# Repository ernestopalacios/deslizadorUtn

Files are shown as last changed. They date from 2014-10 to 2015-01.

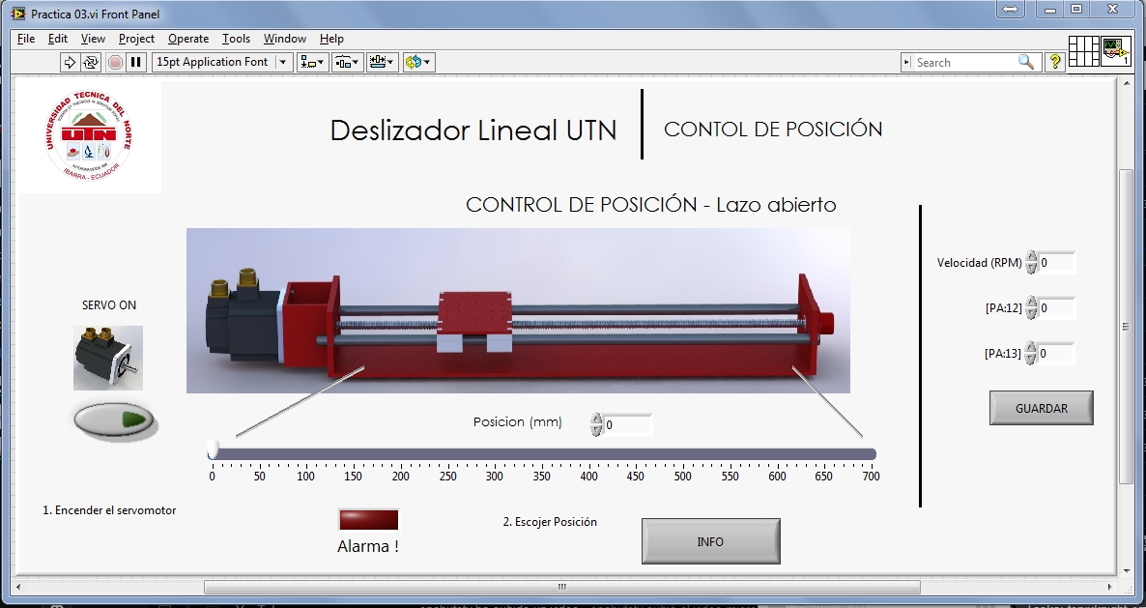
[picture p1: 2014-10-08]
deslizador/SolidW_Final/Renders/Programa/Practica 03.png

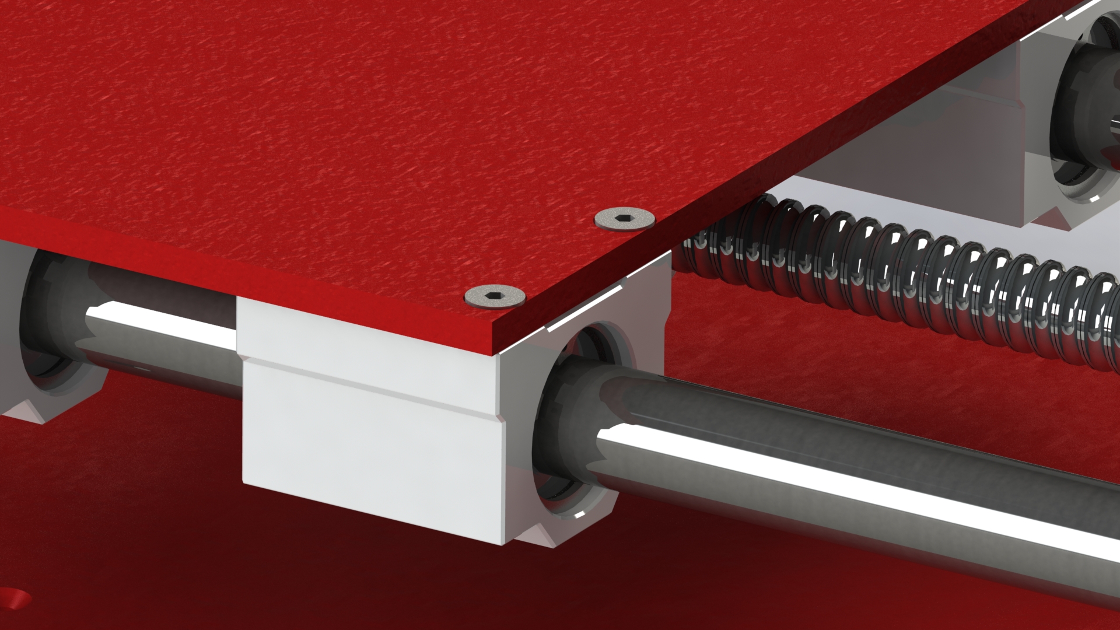
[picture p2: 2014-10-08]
deslizador/SolidW_Final/Renders/detalle_02.JPG

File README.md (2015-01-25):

DeslizadorUtn
=============

Repositorio para el deslizador lineal desarrollado para la Universidad Técnica del Norte.

Manual de ayuda: https://github.com/ernestopalacios/deslizadorUtn/wiki

El reposito esta dividido en las siguientes carpetas:

---> deslizador :  Archivos del deslizador en SolidWorks 2013

---> deslizadorlineal : Documentación del trabajo de grado.

---> labview : Libreria para el control del servomotor en LABVIEW.

---> mbed : Documentacion microcontrolador.

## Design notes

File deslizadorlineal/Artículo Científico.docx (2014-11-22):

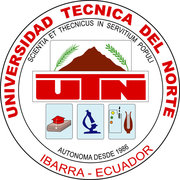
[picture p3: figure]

UNIVERSIDAD TÉCNICA DEL NORTE

FACULTAD DE INGENIERÍA EN CIENCIAS APLICADAS

CARRERA DE INGENIERÍA EN MECATRÓNICA

ARTÍCULO CIENTÍFICO

TEMA:

SISTEMA MODULAR PARA REALIZAR PRÁCTICAS DE SERVOMECANISMOS Y CONTROL MEDIANTE DESLIZADOR LINEAL E INTERFAZ CON LABVIEW

AUTOR: Ernesto Vladimir Palacios Merino

DIRECTOR: Ing. Diego Terán

Ibarra - Ecuador

2014

[^1]

SISTEMA MODULAR PARA REALIZAR PRÁCTICAS DE SERVOMECANISMOS Y CONTROL MEDIANTE DESLIZADOR LINEAL E INTERFAZ CON LABVIEW

Palacios Merino, Ernesto Vladimir

mecatronica.mid@gmai.com

Universidad Técnica del Norte

Resumen—El presente trabajo describe el diseño e implementación de un deslizador lineal, el mismo que ha sido acoplado para su uso con el servomotor GSK 110SJT. Para llevar a cabo el control de este mecanismo se han creado librerías e interfaces en el lenguaje de programación gráfico de LabVIEW, dichas librerías han sido elaboradas con el ánimo de que brinden a los estudiantes de mecatrónica de la Universidad Técnica del Norte, facilidad de uso y escalabilidad en sus proyectos, animando a la creación de programas y mecanismos más elaborados. Una vez que se ha completado la parte mecánica, eléctrica y electrónica se cuenta con un sistema, en el cual se interrelacionan todos sus módulos y subsistemas, a través de una librería y protocolos de comunicación definidos, pudiendo de esta manera llevar a cabo prácticas de servomecanismos y control.

Índice de Términos—LabVIEW (Plataforma de desarrollo virtual gráfico). API (Application Programming Interface)

E

# I. INTRODUCCIÓN

l presente trabajo de grado describe el diseño e implementación de un sistema modular para realizar prácticas de servomecanismos y control. El objetivo del mismo es que tener mayor facilidad de uso de los para los servomotores GSK 110SJT, se han desarrollado cuatro prácticas en las cuales los estudiantes podrán familiarizarse con el sistema y con el control que se puede ejercer sobre la misma.

El recorrido del deslizador es de 80 centímetros dentro de los cuales se ha destinado dos sensores ópticos a cada extremo del deslizador los cuales sirven de advertencia y protección ante eventuales colisiones que puedan sucederse por una mala operación del equipo.

El sistema electrónico permite el control del servodrive a través de una comunicación serial RS-232, o mediante una red de datos TCP/IP. Estas dos formas de comunicación brindan gran flexibilidad en el manejo del dispositivo.

El sistema se subdivide en tres partes claramente diferenciadas, el subsistema mecánico, el subsistema electrónico y el subsistema informático. En la base del subsistema mecánico se encuentra el tornillo de bolas re-circulantes, el cual junto a las guías y rodamientos permiten el movimiento lineal del deslizador. El tornillo utilizado permite tener una precisión de 52um, el servomotor utilizado cuenta con 10 000 pasos por revolución, lo que se traduce a una precisión de 0.5um, la cual se ve limitada por la precisión del tornillo.

El segundo subsistema, el electrónico, cuenta como elemento principal el microcontrolador ARM mbed® el cual actúa como puente entre el subsistema informático y el subsistema mecánico, este elemento permite la ejecución de comandos enviados a través de sus interfaces seriales, o de su interfaz ethernet, permitiendo el control del deslizador de una manera sencilla.

El subsistema informático es aquel que se encuentra expuesto directamente al usuario, se ha creado para ello una interfaz para su programación (API), mediante la cual se puede interactuar con el servomotor y consecuentemente con el deslizador, esta API se ha desarrollado sobre el lenguaje de programación de LabVIEW, sin embargo debido a la característica de comunicación serial del dispositivo estas librerías pueden ser exportadas a otros lenguajes de programación.

# II. Desarrollo de Contenidos

## A. Diseño del sistema

La transmisión de potencia desde el servomotor hacia el carro deslizador se lo realiza a través del tornillo central, el cual se ha determinado como un tornillo de bolas re-circulantes el cual permitirá contar con la precisión necesaria para la implementación de este trabajo, además de minimizar el juego existente entre la tuerca y el tornillo.

Para facilitar el movimiento del carro deslizador se ha escogido rodamientos lineales, los cuales proveen de un bajo coeficiente de fricción además de soportar la fuerza ejercida por la carga. Estos rodamientos requieren de guías de acero rectificado las cuales brindarán una larga vida útil a los rodamientos.

La estructura para soportar el mecanismo se ha elaborado en acero ASTM A-500, permitiendo soportar todas las fuerzas generadas y brindando la rigidez necesaria para el buen desempeño del deslizador para la carga propuesta la cual es de 30 Kg.

## B. Características mecánicas.

El rodamiento lineal escogido es el SKF LBBR 20, el cual soporta una carga estática de 800 Newtons. El tiempo de vida útil calculado para una carga de 588 Newtons es de 176 Km de recorrido de acuerdo a la siguiente ecuación:

L_10 =(l_s)/(l_t)(C/P)^p L_10 =0.7/1(800/588)^3

L_10 =1.76 ∙10^5 (m)

Se ha utilizado dos rodamientos por guía, con un total de cuatro rodamientos. El tornillo tiene una longitud total de 1000 mm, un diámetro externo de 16 mm y una longitud de paso de 5mm, se cuenta con una eficiencia del 90% y un coeficiente de fricción de 0.05% con lo cual cumple con los requisitos necesarios para esta aplicación.

Para calcular la inercia del eje contamos con la siguiente fórmula:

J_(eje) =(7.57x10^(-13) )D^4 L kg-m^2

Dónde.

J = Inercia en el eje

D = Diámetro del eje

L = Longitud del eje

Utilizando los valores de la hoja de datos del tornillo obtenemos:

J_(eje) =(7.57x10^(-13) )(16)^4 (1000) (kg.m^2 ) J_(eje) =4.96x10^(-5) (kg.m^2 )

La inercia de la carga es la siguiente:

J_(eje) =(2.25x10^(-8) )(m_(carga))/(P^2) kg-m^2

Dónde.

J_(carga) = Inercia de la carga reflejada en kg.m2

m_(carga) = Carga útil en kg a:

P = paso del eje expresado en rev/mm

Utilizando los valores de este proyecto tenemos:

J_(eje) =(2.25x10^(-8) )30/(0.2^2) ( kg.m^2 ) J_(eje) =1.6875 x 10^(-5) (kg.m^2 )

J_(eje) =(7.57x10^(-13) )(16)^4 (1000) (kg.m^2 ) J_(eje) =4.96x10^(-5) (kg.m^2 )

J_(TOTAL) =(1.6875+4.96)x10^(-5) (kg.m^2 ) J_(TOTAL) = 6,6475 ( kg.m^2 )

El torque para la aceleración, tomando en cuenta la carga utilizada, la inercia en el motor y la eficiencia obtenemos el siguiente resultado.

T_α =(J_(motor) +(J_(eje))/e+(J_(carga))/e)α N.m

Dónde:

e = Eficiencia

J_(motor) = Inercia del motor (típico 0.5)

T_α =(0.5+6.6475/0.9)x10^(-5) (11310) (N.m) T_α =0,89 (N.m)

El torque generado por el servomotor es de dos Newton por metro, con lo cual podrá funcionar sin ningún inconveniente.

## C. Características electrónicas.

El subsistema electrónico tiene como base al microcontrolador LPC1768 el cual implementa la plataforma de desarrollo ARM mbed. Este microcontrolador interactúa con el servodrive mediante señales eléctricas, el servodrive es el elemento que controla al servomotor. El microcontrolador está conectado al encoder y a los sensores de proximidad del deslizador.

Los sensores de proximidad están colocados de tal manera que el carro deslizador no golpee los extremos del deslizador y evite que sea dañado por una mala manipulación. Se ha implementado un sensor de advertencia y uno de error para cada extremo del deslizador, esto permite al programador tomar acciones correctivas y de no hacerlo el sensor de error actúa y detiene al servomotor.

El encoder implementado es un encoder absoluto de cuadratura HOHNER, el cual cuenta con una resolución de 360 pulsos por revolución, al ser conectado al microcontrolador puede multiplicar la resolución por cuatro, esto se puede lograr debido a los dos canales, A y B del encoder dando una resolución de 1440 pulsos por resolución, lo cual se traduce a una precisión de 3.472 micrones.

El subsistema electrónico tiene dos fuentes de energía una de 24 VDC y otra de 5 VDC, la fuente de 24 VDC se utiliza para la alimentación del encoder y la generación de una señal analógica de voltaje para el control de velocidad del servomotor, la fuente de 5 VDC es utilizada para la alimentar el microcontrolador.

El microcontrolador implementa para la comunicación dos puertos seriales, uno a través de USB y otro a través de un conector DB-9, también se implementa un puerto de comunicaciones ethernet, con el cual se puede conectar el microcontrolador a una red de datos cableada.

## D. Características de software

Las opciones de comunicación implementadas por el microcontrolador simplifican en gran medida el control del servomotor, tomando ventaja de este hecho se ha diseñado un listado de comandos que el microcontrolador puede ejecutar para el control del servomotor.

TABLA I

Listado de comandos para la comunicación con el microcontrolador ARM MBED
Comando | Valores aceptables | Detalle
S | 0 a 1 | Apagar / Encender el servomotor
H | 0 a 500000 | Frecuencia de salida del tren de pulsos, en hertzios.
K | 0 a 500 | Frecuencia de salida del tren de pulsos, en kilohertzios.
D | 0 a 1 | Sentido de giro: (CW = 1 – Hacia el motor). (CCW = 0 – Hacia el encoder).
A | -10000 a +10000 | Voltaje de salida de +-10V con una resolución de ~4.8mV.
P | 0 a 2 147 483 647 | Número predefinido de pulsos
M | 0 a 2 147 483 647 | Generar un número predefinido de pulsos, multiplica el valor del comando por mil
N | 0 a 2 147 483 647 | Generar un número predefinido de pulsos, multiplica el valor del comando por un millón
V | 10 - 500000 | La velocidad en tren de pulsos a la cual se va a llegar al ángulo deseado para el eje del motor.
I | 0 a 2 147 483 647 | Lleva el carro al inicio del recorrido. El valor numérico determina la frecuencia del tren de pulsos
E | 0 a 1 | 0 Leer posición actual. 1 Leer velocidad actual.
Z | 0 | Limpia el contador del encoder

El microcontrolador ejecutará estos comandos siempre y cuando lleguen en el formato correcto.

[int32]-[Comando][Enter]

[int32] = Cualquier número entero de 32bits.

[Comando] = Letra mayúscula que designa una acción a realizar.

[Enter] = Carácter Retorno de carro para enviar el comando.

Ejemplo de comandos aceptables:

1500-H

-125000000-P

0-E

-1-R

Se ha implementado una librería en el lenguaje de programación LabVIEW que permite a los estudiantes la interacción con el servomotor, esta librería actúa como una Interfaz de programación sobre la cual los estudiantes pueden desarrollar sus proyectos.

Esta librería se ha desarrollado en dos versiones, una para la comunicación serial y una para la comunicación ethernet, lo que permite esta librería es tener bloques de programación sencillos con los cuales se puede elaborar programas más complejos.

# III. Resultados Obtenidos

Mediante la aplicación de todo lo hasta aquí expuesto se tiene el resultado final el cual se muestra a continuación.

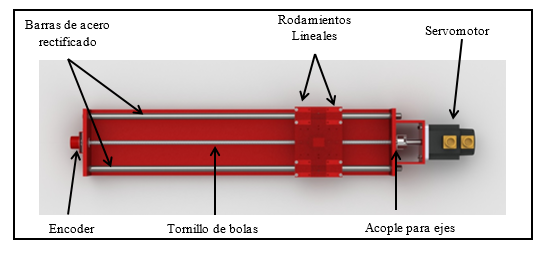
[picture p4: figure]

Fig. 1. Subsistema Mecánico.

El subsistema mecánico ensamblado, el servomotor es sujetado a la estructura del deslizador y unido al tornillo central mediante el uso de un matrimonio mecánico, de esta manera el tornillo central girará conjuntamente con el eje del servomotor. El carro deslizador se encuentra sujeto a la nuez del tornillo transmitiendo el torque rotacional del servomotor en movimiento, el peso que se aplica sobre el carro deslizador mismo es soportado por las guías laterales sobre las cuales se montan los rodamientos lineales facilitando su movimiento. Al final del tornillo de bolas se ubica el encoder, el cual gira junto con el eje del tornillo y del servomotor sirviendo de esta manera como sensor de retroalimentación al sistema.

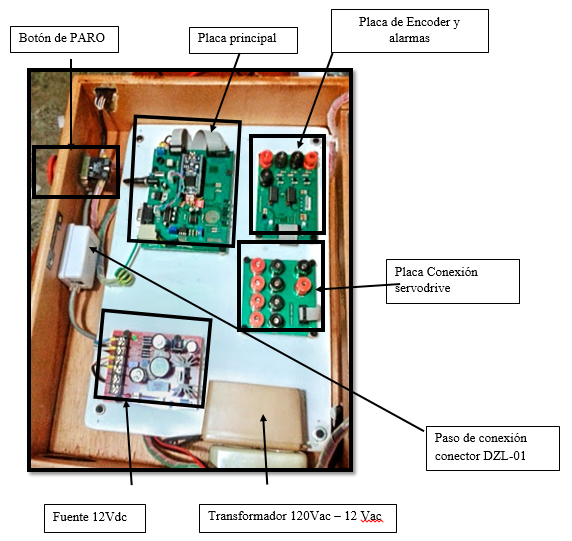
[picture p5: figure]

Fig. 2. Subsistema Electrónico

La implementación del subsistema electrónico cuenta con tres placas electrónicas, cada una desempeñando una función específica. La primera es la placa de conexión con el servodrive, la cual sirve para realizar las conexiones eléctricas con el servodrive. La segunda es la placa de encoder y alarmas, esta tiene la función de conectar el encoder y los sensores de proximidad ópticos, adapta su voltaje e implementa un circuito de protección independiente al microcontrolador principal para los casos en los que el carro del deslizador se acerque demasiado a los extremos del servomotor. Finalmente tenemos nuestra placa principal que es aquella en la que está montado el microcontrolador, en esta se tiene los puertos de comunicación con los dispositivos exteriores y en la cual se configura el modo de operación del subsistema.

El subsistema cuenta con dos modos de comunicación, serial y ethernet, sin embargo el microcontrolador solo puede trabajar con uno de ellos a la vez, por tal motivo es necesario configurar el puerto con el cual se va a trabajar. Para el modo de comunicación serial tenemos dos puertos, USB y conector DB-9, el puerto USB puede ser conectado directamente a un computador, sin embargo la longitud del cable queda restringida al estándar USB, para superar este problema se encuentra implementado el puerto DB-9, el cual cumple con los estándares RS-232 y puede ser extendido hasta una longitud de varios metros, dependiendo de la protección del cable utilizado. En el modo de comunicación ethernet se tiene un conector RJ-45 el cual permite al dispositivo ser conectado a un ruteador con el protocolo DHCP habilitado para que de esta manera el dispositivo pueda obtener una dirección IP válida y se pueda realizar la comunicación con el microcontrolador.

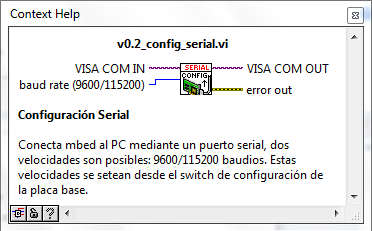
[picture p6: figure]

Fig. 3. Subsistema de Control

Finalmente tenemos el subsistema de control, implementado a través de la API creada para este efecto, la misma que ha sido desarrollada para el lenguaje LabVIEW. Esta librería permite controlar todos los aspectos fundamentales del dispositivo y ha sido escrita en dos versiones, una para cada modo de comunicación, tenemos la librería de comunicación serial y la librería de comunicación ethernet. Ambas librerías son simétricas, es decir que por cada función implementada en la librería serial se tiene su contraparte en la librería ethernet.

Además del control básico de los comandos enviados al servomotor estas librerías poseen funciones de reconocimiento de errores y generación de alarmas, lo cual facilita al estudiante el tomar acciones correctivas de acuerdo a los eventos generados.

Una vez que sistema modular se encuentra operativo se realizó algunas pruebas para comprobar el correcto funcionamiento de todos los subsistemas, encontrándose los siguientes resultados.

Tabla II

Pruebas de posición
N° Prueba | Carga (Kg) | Error medido (mm)
1 | 0 | > 0.01
2 | 5 | > 0.01
3 | 10 | > 0.01
4 | 15 | > 0.01
5 | 20 | > 0.01
6 | 25 | > 0.01
7 | 30 | > 0.01

El servomotor cuenta con dos modos de funcionamiento, uno de control de posición el cual es muy preciso y un modo de control de velocidad, para aplicaciones en las que se requiere de un torque constante.

En la Tabla 1 se analiza el error medido cuando el deslizador es sometido a diferentes cargas, obteniendo un resultado mejor al requerido por el alcance de nuestra aplicación. Esto es completamente esperado debido a la precisión tanto del servomotor como al juego casi inexistente en el tornillo.

Tabla III

Pruebas de velocidad
Voltaje aplicado (Vdc) | Velocidad esperada | Velocidad Medida (RPM)
10.00 | 2000 | 2000
5.00 | 1000 | 1150
2.00 | 400 | 452
1.00 | 200 | 218
0.00 | 0.00 | 0
-1.00 | -200 | -217
-2.00 | -400 | -450
-5.00 | -1000 | -1150
-10.00 | -2000 | -2000

En el modo de control de velocidad el servomotor se controla por medio de una salida de voltaje, para las mediciones se ocupó un multímetro FLUKE 83V calibrado con una precisión de cuatro cifras significativas, la medición de la velocidad fue tomada mediante el sensor del servodrive y se desconectó el carro deslizador del tornillo para tomar varias mediciones sin que el carro golpeé el final del deslizador. En este caso se puede apreciar que la velocidad medida no corresponde exactamente con el valor esperado, esto puede deberse a que el sensor de voltaje en el servodrive se encuentra descalibrado. Este error inherente en el servomotor abre la posibilidad de implementar métodos de control que permitan estudiar, minimizar y eliminar el error con el control de velocidad del sevomotor.

# IV. Practicas

El objetivo de este proyecto es la utilización del sistema modular por parte de los estudiantes, por tal motivo se ha desarrollado cuatro prácticas con las cuales se espera que el estudiante se familiarice con el manejo y programación del módulo. Estas prácticas exponen al estudiante con todas las posibilidades brindadas por el sistema y alientan a su modificación y observación de resultados. Todas las prácticas se ofrecen a través del modo de comunicación serial.

## A. Práctica 01. Generación de frecuencia

En la primera práctica se presenta al estudiante con el control del servomotor en su modo de posición. En este modo de control el subsistema electrónico genera un tren de pulsos, la frecuencia de este tren de pulsos determina la velocidad del servomotor, la dirección del giro es controlada por una salida digital.

El estudiante es presentado con una interfaz de fácil manejo en la cual controlan el encendido y apagado del servomotor, la frecuencia del tren de pulsos generados, y la dirección de giro del servomotor.

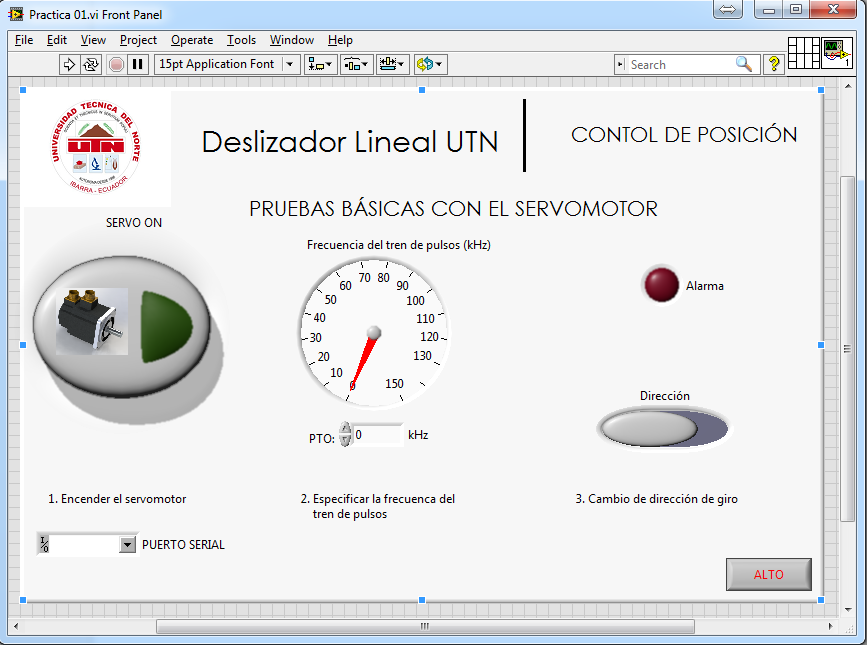
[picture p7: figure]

Fig. 4. Panel Frontal – Control de Posición.

Para el correcto funcionamiento de la práctica se requiere que el estudiante configure de manera adecuada los parámetros del servomotor, la comunicación serial y las conexiones eléctricas del servodrive, para completar estos pasos es necesario que el estudiante conozca estos aspectos básicos del sistema con lo cual se tiene una introducción a los conceptos básicos del manejo del servomotor y del sistema que se ha diseñado para su control.

## B. Práctica 02. Generación de voltaje

Esta práctica es similar a la primera práctica, sin embargo el modo de funcionamiento del servomotor es control de velocidad, en esta práctica el subsistema electrónico genera una señal de voltaje variable que controla la velocidad rotacional del servomotor.

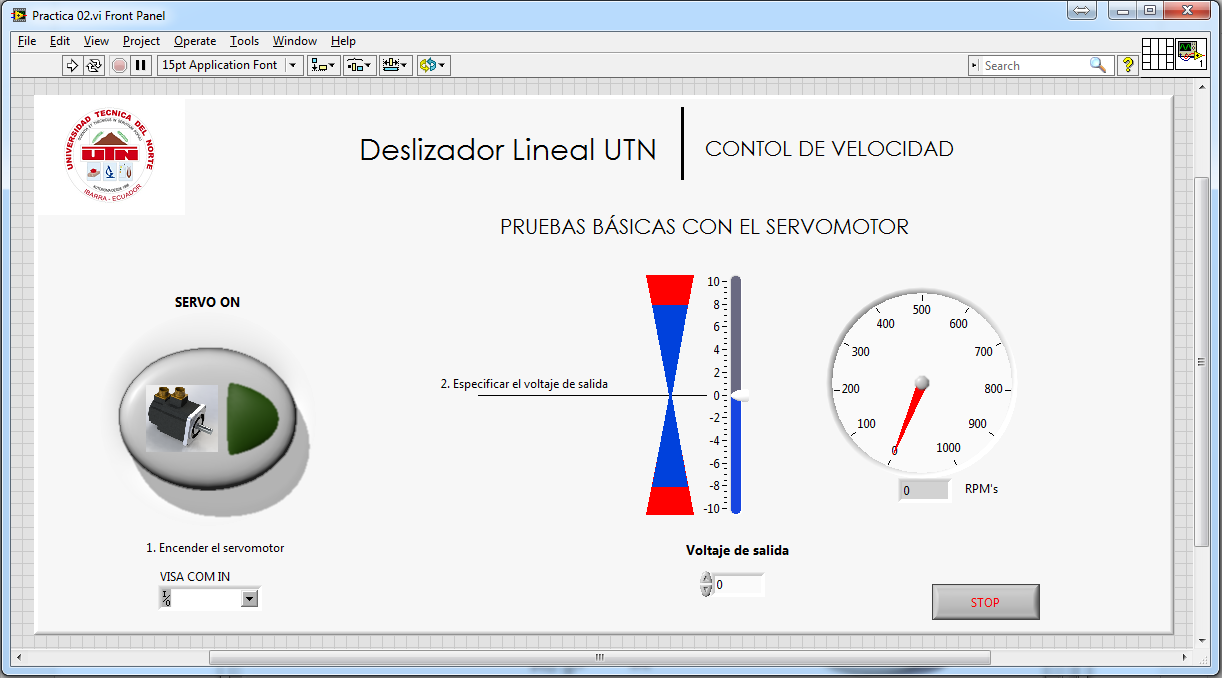
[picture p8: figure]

Fig. 5. Panel Frontal – Control de velocidad.

Este tipo de control se utiliza para alcanzar altas velocidades con el servomotor, el voltaje generado puede llegar a tener un valor máximo de +/- 10 Vdc. En esta práctica se tiene un control de lazo abierto, se tienen un deslizador para controlar el voltaje de salida y un tacómetro el cual indica la velocidad medida por el encoder en revoluciones por minuto.

## C. Practica 03. Control de Posición

La práctica número tres es una práctica en la cual se busca posicionar el carro deslizador de una manera precisa y dinámica en un punto determinado del recorrido deslizador. Para ello se hace uso del generador de frecuencia del microcontrolador para generar un número determinado de pulsos y de esta manera desplazar el carro una distancia definida.

El mecanismo utilizado para la generación de pulsos es mediante un cronómetro el cual lleva la cuenta del tiempo que se han generado pulsos y calcula la posición en la cual se encuentra el carro. Este es un proceso de lazo abierto, el programa en LabVIEW asume que el carro se ha desplazado una determinada distancia dependiendo del tiempo que ha transcurrido en su cronómetro interno.

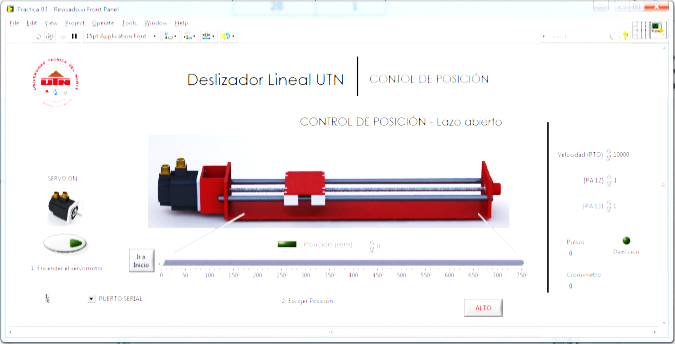
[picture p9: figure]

Fig. 6. Panel Frontal – Control de Posición.

En esta practica el control de posición es dinámico, es decir que la posición final del carro puede cambiar de manera aleatoria, esto se ha tomado en cuenta en la programación de la practica, cuando la posición de llegada del carro cambia el programa calcula cuanto tiempo ha transcurrido desde la última vez que se llegó a la posición final y dependiendo de la frecuencia del tren de pulsos calcula la posición actual y cuanto tiempo debe transcurrir hasta llegar a la nueva posición final. Mediante la aplicación de este algoritmo se incurre en un error cada vez que se calcula una nueva posición, ya que el algoritmo no toma en cuenta el tiempo transcurrido mientras se realiza el cálculo. Este error, aunque es mínimo debido a la velocidad de procesamiento de los computadores actuales, es acumulativo y cuando se generan altas frecuencias puede llegar a afectar notablemente la precisión del deslizador.

Existen varios métodos para corregir este error, y se alienta al estudiante a explorar las opciones y experimentar con los resultados obtenidos.

## D. Práctica 04 – Control de velocidad

La última práctica tiene como objetivo demostrar las capacidades de control en lazo cerrado del sistema, utilizando como sensor de retroalimentación al encoder. Este se utiliza para medir la velocidad rotacional del servomotor y realizar los ajustes necesarios para obtener la velocidad seteada.

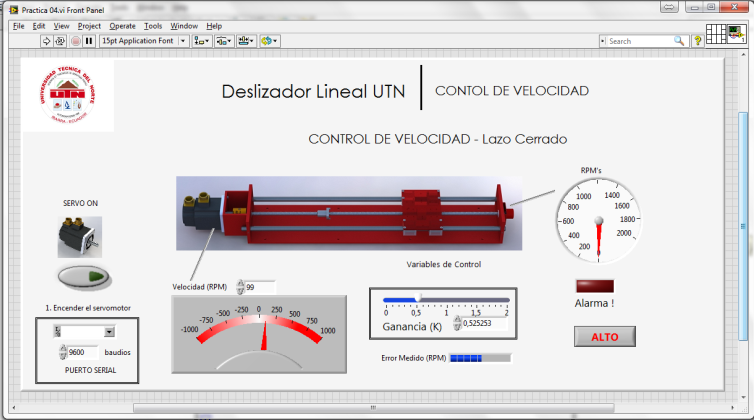
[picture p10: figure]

Fig. 7. Panel Frontal – Control de Velocidad

Para el lazo de cerrado se utiliza un control proporcional el cual puede ser modificado durante la ejecución del programa permitiendo experimentar con este tipo de control y observar de manera experimental los efectos que tiene este control sobre la salida de nuestro sistema.

# V. CONCLUSIONES

- Se ha determinó que la velocidad máxima soportable por el mecanismo es de 1500 RPM, una velocidad superior por un periodo prolongado de tiempo puede provocar daños a los rodamientos del deslizador.
- Se diseño un sistema que puede ser usado por una amplia gama de estudiantes, no es estrictamente necesario tener conocimientos avanzados en servomecanismos.
- Las librerías creadas en el entorno de desarrollo permiten una programación del deslizador que se acople a las diferentes prácticas del deslizador.
- Se logró un diseño robusto adecuado para soportar posibles abusos por parte de los estudiantes en sus experimentos.
- El módulo se implementó con medidas de seguridad que permiten la colisión de la mesa de trabajo con los extremos del deslizador. Además de un botón de paro de emergencia en caso de ser necesario.

# VI. Sugerencias

- Se deben observar todas las precauciones de seguridad al momento de operar el módulo para asegurar una larga vida útil del mismo.
- Se sugiere la implementación de puesta tierra para todos los equipos del laboratorio de electrónica y mecatrónica.
- La programación tanto de la librería de funciones en LabVIEW como la del microcontrolador son de código abierto, se sugiere su estudio y mejoramiento de los algoritmos implementados en el módulo.
- El módulo puede ser controlado desde Matlab, se sugiere la implementación de lazos de control en este programa como un ejemplo práctico de sus capacidades de programación.
- La mesa del deslizador tiene la capacidad de atornillar diferentes tipos de mecanismos adicionales, se sugiere el montaje de un brazo robótico que permita la manipulación de objetos.

# referencias

[1] Beer, F., & Johnston, R. (2010). MECÁNICA VECTORIAL PARA INGENIEROS. México: McGraw Hill.
[2] Sharp, R. (2008). Principles of Protocol Design. Kongens Lyngby: Springer.
[3] Blanding, D. L. (1995). Machine Design Using Kinematics Processing. New York: The American Socierty of Mechanical Engineers.
[4] NSK Corporation. (2005). What is a ball screw? Franklin.
[5] Scolum, A. H. (1992). Precision machine design. New Jersey: Prentice-Hall, Inc.
[6] GSK CNC Equipment Co. (2007). DA98D Digital AC Servo Drive Unit. Guanzhou.
[7] Hihglights. (2011). CONVERSIÓN DE SEÑAL DE ENCODER DE CUADRATURA . Cuenca, Ecuador.
[8] León Aguirre, A., & Tapia Vaca, J. (2009). Sincronismo y supervisión de posición y velocidad de un motor trifásico asíncrono con un sistema de encoders maestro-esclavo para aplicaciones de control de ejes. Latacunga: Escuela Politécnica del Ejercito.
[9] SKF Group. (20 de Enero de 2014). www.skf.com. Obtenido de http://www.skf.com/binary/12-55835/SKF4182_EN_Linear-ball-bearings.pdf
[10] THK. (2010). Guide Ball Bushing / Linear Bushing. Agoura Hills: THK.
[11] Hohner Corporation. (20 de Enero de 2014). www.encoderonline.com. Obtenido de http://www.encoderonline.com/Devicenet/Data-Sheets/Incremental/Data-33.htm
[12] Márquez Días, J., Pardo Sánchez, K., & Pizarro Valencia, S. (10 de Enero de 2014). http://rcientificas.uninorte.edu.co/. Obtenido de http://rcientificas.uninorte.edu.co/index.php/ingenieria/article/view/2272/1484
[13] Microsoft. (24 de 11 de 2013). http://technet.microsoft.com/. Obtenido de http://technet.microsoft.com/en-us/library/cc759499(v=ws.10)
[14] Zuñiga Tufiño, M. A. (2008). ESTUDIO DISEÑO Y SIMULACIÓN DE UN SISTEMA DE. Quito: ESCUELA POLITECNICA NACIONAL.
[15] Aerotech. (20 de Enero de 2014). www.aerotech.com. Obtenido de http://www.aerotech.com/media/247221/section16_motor%20selection%20and%20sizing.pdf

Autor

Ernesto Palacios Merino, estudiante de mecatrónica en la Universidad Técnica del Norte, oriundo de la ciudad de Loja. Actualmente se encuentra trabajando en la empresa Kradac, en el área de robótica.

UNIVERSIDAD TÉCNICA DEL NORTE

FACULTAD DE INGENIERÍA EN CIENCIAS APLICADAS

CARRERA DE INGENIERÍA EN MECATRÓNICA

SCIENTIFIC ARTICLE

TOPIC:

MODULAR SYSTEM FOR CONTROL AND SERVOMECHANISMS PRACTICES USING A LINEAR SLIDER WITH A LABVIEW INTERFACE

AUTHOR: Ernesto Vladimir Palacios Merino

DIRECTOR: Ing. Diego Terán

Ibarra - Ecuador

2014

[^2]

MODULAR SYSTEM FOR CONTROL AND SERVOMECHANISMS PRACTICES USING A LINEAR SLIDER WITH A LABVIEW INTERFACE

Palacios Merino, Ernesto Vladimir

mecatronica.mid@gmail.com

Universidad Técnica del Norte

Abstract— This paper describes the design and implementation of a linear slider; it has been design for use with GSK 110SJT servomotor. To implement the control for this mechanism have been established libraries and interfaces in the graphical programming language LabVIEW, these libraries have been produced with the intention to provide students of Mechatronics in the "Universidad Técnica del Norte" usability and scalability in their projects, by encouraging the creation of programs and elaborated mechanisms. Once the mechanical, electrical and electronics parts have been completed the students will have a system in which all these modules and subsystems are interrelated through a software library and defined communication protocols, and can thus carry out practices and servo control..

Glossary — LabVIEW (Graphic visual development platform). API (Application Programming Interface)

T

# VII. INTRODUCTION

his paper describes the design and implementation of a modular system for servo and control practices. The objective is to have greater ease of use for GSK 110SJT servo motor, four practices have been developed in which students can become familiar with the system and the control that can be exerted on it.

The slider travel is 80 centimeters, inside of which there has being allocated two optical sensors at each end of the slider which serve as warning and protection against possible collisions that could be caused by poor equipment operation.

The electronic system allows control over the servo drive via a serial RS-232, or via a TCP / IP connection. These two forms of communication offer great flexibility for handling the device.

The system is divided into three distinct parts, the mechanical subsystem, the electronic subsystem and the computer subsystem. On the basis of the mechanical subsystem is a ballscrew, which together with the linear guides and bearings allow linear movement of the slider. The ballscrew used has an accuracy of 52um, the servo used has 10,000 steps per revolution, which translates to a precision of 0.5um, this precision is limited by the accuracy of the ballscrew.

The second subsystem, has as its main element an ARM mbed® microcontroller which acts as a bridge between the computer subsystem and the mechanical subsystem, this element allows the execution of commands via their serial interfaces, or the ethernet interface, allowing control of the slider in a simple manner.

The computer subsystem is the one that is exposed directly to the user, for this an application programming interface (API) was created, through which you can interact with the servo and consequently with the slider, this API was developed on the LabVIEW programming language, however due to the serial communication characteristic of the device such libraries can be exported to other programming languages.

# VIII. Content Development

## A. System Design

The transmition of power from the servomotor to the slider is performed through the central ballscrew, which has been determined as a ballscrew with re-circulating balls which will allow for the precision necessary in the implementation of this work, in addition to minimize the clearance between the nut and screw, referred as backslash.

To facilitate movement of the slider carriage linear bearings have been chosen, which provide a low friction coefficient in addition to support for the force exerted by the load. These bearings require rectified steel guides which provide long life to the bearings.

The structure for supporting the mechanism is made of steel ASTM A-500, allowing withstand all the forces generated and providing the necessary rigidity for the proper performance of the slider to the weight proposed which is 30 Kg.

## B. Características mecánicas.

The linear Bearing chosen is SKF LBBR 20, which supports a static load of 800 Newtons. The estimated lifetime for a load of 588 Newtons is 176 km in length according to the following equation:

L_10 =(l_s)/(l_t)(C/P)^p L_10 =0.7/1(800/588)^3

L_10 =1.76 ∙10^5 (m)

We used two bearings for each guide, with a total of four bearings. The screw has an overall length of 1000 mm, an outer diameter of 16 mm and a pitch length of 5 mm, the efficiency is 90% and a coefficient of friction of 0.05% thus meets the requirements for this application. To calculate the inertia on the shaft following formula has been used:

J_(eje) =(7.57x10^(-13) )D^4 L kg-m^2

Where,

J = Axis Inertia

D = Axis diameter

L = Axis length

Using the values provided by the datasheet we get:

J_(eje) =(7.57x10^(-13) )(16)^4 (1000) (kg.m^2 ) J_(eje) =4.96x10^(-5) (kg.m^2 )

The inertia on the load is:

J_(eje) =(2.25x10^(-8) )(m_(carga))/(P^2) kg-m^2

Where.

J_(carga) = Inertia on the load in kg.m2

m_(carga) = Useful load in kg a:

P = ballscrew step in rev/mm

Using the data of the Project we get:

J_(eje) =(2.25x10^(-8) )30/(0.2^2) ( kg.m^2 ) J_(eje) =1.6875 x 10^(-5) (kg.m^2 )

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

J_(TOTAL) =(1.6875+4.96)x10^(-5) (kg.m^2 ) J_(TOTAL) = 6,6475 ( kg.m^2 )

The initial torque necessary for acceleration, calculated using the load, the servomotor inertia and the efficiency of the system we obtain the following result.

T_α =(J_(motor) +(J_(eje))/e+(J_(carga))/e)α N.m

Where:

e = Efficiency

J_(motor) = Servomotor Inertia (typical 0.5)

T_α =(0.5+6.6475/0.9)x10^(-5) (11310) (N.m) T_α =0,89 (N.m)

The torque generated by the servomotor is two Newton by meter, which is superior to the torque needed for the system to work.

## C. Electronic characteristics.

The electronic subsystem is based on the LPC1768 microcontroller which implements the ARM mbed development platform. This microcontroller interacts with the servo drive using electrical signals; the servo drive is the element that controls the servomotor. The microcontroller is connected to the encoder and proximity sensors.

Proximity sensors are positioned so that the car does not hit the slider end and prevent it from being damaged by rough handling. We have implemented one warning sensor and one error sensor for each end of the slider; this allows the programmer to take corrective action, if none is taken the error sensor acts and stops the servomotor.

The implemented encoder is a HOHNER absolute quadrature encoder, which has a resolution of 360 pulses per revolution, it's connected to the microcontroller and the resolution can be multiplied by four, this can be achieved due to the two channels, A and B of the encoder giving a resolution of 1440 pulses per resolution, which translates to a precision of 3.472 microns.

The electronic subsystem has two power sources, one of 24 VDC and the other of 5 VDC, 24 VDC supply is used to power up the encoder and generating an analog voltage signal for the speed control of the servo motor, the source of 5 VDC is used to power the microcontroller.

The microcontroller implements two serial ports, one through USB and one through a DB-9 connector, there is another means of communication, an ethernet communications port through which the microcontroller can be connected to a wired network.

## D. Software characteristics

Communication options implemented by the microcontroller greatly simplify servo control, taking advantage of this fact a list of commands have been designed so that the microcontroller can run them for servo motor control.

The microcontroller will execute these commands provided that they arrive with the correct format.

This library has been developed in two versions, one for serial communication and one for Ethernet communication, which allows this library to have simple programming blocks which can develop more complex programs.

A LabVIEW programming library has been design that allows students to interact with the servomotor, this library acts as a programming interface on which students can develop their projects.

TABLE I

List of the commands for the communication with the ARM Mbed microcontroller
Command | Acceptable Values | Detail
S | 0 to 1 | On/Off for the servomotor
H | 0 to 500000 | Pulse Train Output in Hertzs
K | 0 to 500 | Pulse Train Output in Kilo Hertzs
D | 0 to 1 | Direction: (1 = Clock wise). (0=Counter Clock wise).
A | -10000 to +10000 | Output voltage +-10V with a resolution of ~4.8mV.
P | 0 to 2147483647 | Generate a defined number of pulses
M | 0 to 2147483647 | Generate a defined number of thousands of pulses
N | 0 to 2147483647 | Generate a defined number of million of pulses.
V | 10 to 500000 | Frequency of the pulse train at for the defined pulses
I | 0 to 2147483647 | Takes the carriage to the beginning of the slide, the number defines the frequency of the pulse train.
E | 0 to 1 | 0 = Reads current position. 1 Reads current speed (RPM).
Z | 0 | Clears encoder counter.

Format of the commands sent to the microcontroller.

[int32]-[Command][Return]

[int32] = integer number 32bits.

[Command] = A letter describing the command to be implemented.

[Return] = Return Carriage (0x13)

Example of valid commands:

1500-H

-125000000-P

0-E

-1-R

# IX. Resultados Obtenidos

Once all of this has been applied, the result is as follows.

Fig. 1. Mechanical Subsystem.

The mechanical subsystem assembly, the actuator is attached to the sled frame and connected to the ballscrew through the use of a mechanical coupling, so the central ballscrew rotates together with the shaft of the servomotor. The slider carriage is subject to the nut of the screw transmitting rotational torque of the servomotor moving weight that is applied to the same slide carriage is supported by the side rails on which the bearings are mounted facilitating their movement. At the end of the ball screw there is an encoder, which rotates together with the screw shaft of the servomotor and thus serving as sensor feedback system is located.

Fig. 2. Electronic subsystem

The implementation of the electronic subsystem has three electronic boards, each performing a specific function. The first board is connected to the servo drive, which is used to make electrical connections to the servo drive. The second is the encoder and alarms board, this serves to connect the encoder and optical proximity sensors, adjusts its voltage and implements an independent circuit protection to the main microcontroller for cases where the slider carriage moves too close to the ends of the actuator. Finally we have our main board the one in which the microcontroller is located, this board has the ports for communication with external devices and in this board is located a switch to configure the operation mode of he microcontroller.

The subsystem has two communication modes, serial and ethernet, though the microcontroller can only work with one at a time, for this reason it is necessary to configure the port with which it will work. For the serial communication mode there is two ports, a USB and a DB-9 connector, the USB port can be connected directly to a computer, but the cable length is restricted to the USB standard, to overcome this problem a DB-9 port has been implemented, which meets RS-232 standards and can be extended to a length of several meters, depending on the protection of the cable used. In Ethernet mode of communication has an RJ-45 connector which allows the device to be connected to a DCHP enabled router so that the device can obtain a valid IP address and provide communication with the microcontroller.

Fig. 3. Subsistema de Control

Finally we have the control subsystem, implemented through the API created for this purpose, the same that has been developed for the LabVIEW language. This library allows control of all key aspects of the device and has been written in two versions, one for each communication mode, the library for serial communication and the library for Ethernet communication. Both libraries are symmetrical, ie that for each function implemented in serial library there is a counterpart in the ethernet library.

Besides the basic control commands sent to the servomotor these libraries have functions for error detection and alarm generation, which helps students taking corrective actions according to events generated.

Once the modular system has been operative some tests were performed to verify the correct operation of all subsystems, and following results were found.

The servomotor has two modes of operation, a position control which is very precise and speed control mode, for applications where it is required that the servomotor maintains a constant torque.

Table 1 shows the measured error analyzed when the slider is subjected to different loads, obtaining a better than required precision by the scope of our application. This is entirely expected because both precision of the servomotor and the almost nonexistent backslash on the ballscrew.

Table II

Position test
N° Trial | Load (Kg) | Measured error (mm)
1 | 0 | > 0.01
2 | 5 | > 0.01
3 | 10 | > 0.01
4 | 15 | > 0.01
5 | 20 | > 0.01
6 | 25 | > 0.01
7 | 30 | > 0.01

TablE III

Speed Test
Applied voltage (Vdc) | Expected Speed (RPM) | Measured Speed (RPM)
10.00 | 2000 | 2000
5.00 | 1000 | 1150
2.00 | 400 | 452
1.00 | 200 | 218
0.00 | 0.00 | 0
-1.00 | -200 | -217
-2.00 | -400 | -450
-5.00 | -1000 | -1150
-10.00 | -2000 | -2000

The control mode for servo motor speed is controlled by means of a voltage output. This voltage was measurement using a FLUKE 83V multimeter calibrated to four significant figures addressed, the speed measurement was taken using the sensor of the servo drive and the slider carriage was disconnected from the ballscrew, this is necessary in order to take multiple measurements without the car hitting the end of the slider. In this case it can be seen that the measured speed does not correspond exactly to the expected value, this may be because the voltage sensor in the servo drive is un-calibrated. This inherent error in the servomotor opens the possibility of implementing control methods to study its results in the system, to minimize and eliminate the error with the speed control sevomotor.

# X. Practicas

The objective of this project is the use of the modular system by students, for this reason four practices has been developed which are expected to familiarize students with the operation and programming of the module. These practices expose the student with all the possibilities offered by the system and encourage modification and observation results. All practices are offered through serial communication mode.

## A. Practice 01. Frequency generation

In the first practice the student is presented with position control of the servomotor. In this control mode the electronic subsystem generates a pulse train, the frequency of this pulse train determines the motor speed, and direction of rotation is controlled by a digital output.

The student is presented with a user-friendly interface in which control the switching on and off of the servomotor, the frequency of the pulse train generated, and the direction of rotation of the servomotor.

Fig. 4. Panel Frontal – Control de Posición.

For proper operation of the practice it is required the student properly configure the parameters of the servo motor, serial communication and servo electrical connections, to complete these steps is necessary for the student to know these basic aspects of the system thereby is an introduction to the basics of servo motor management.

## B. Practice 02. Voltage generation

This practice is similar to the first one, however the operation mode is speed control, in this practice the electronic subsystem generates a variable voltage signal that controls the rotational speed of the servomotor.

Fig. 5. Frontal Panel – Speed Control

This type of control is used to achieve high-speed, the voltage generated can have a maximum of +/- 10 Vdc. This practice has an open-loop control, it has a slider to control the output voltage and a tachometer which indicates the speed measured by the encoder in RPM.

## C. Practice 03. Position Control

The practice number three is a practice which seeks to position the slider carriage accurately and dynamically at a given point of the slider travel. This makes use of the microcontroller frequency generator, it is used to generate a number of pulses and thus move the carriage a defined distance.

The mechanism for generating pulses is by a timer which keeps track of time pulses that have been generated and calculates the position in which the carriage is. This is an open-loop process, the LabVIEW program assumes that the car has traveled a certain distance depending on the time that has elapsed in its internal timer.

Fig. 6. Frontal Panel – Position Control.

In this practice the position control is dynamic, meaning that the final position can change at random, this was taken into account when programming the practice, when the arrival position of the carriage changes the program calculates how long it has elapsed since the last time they reached the final position and depending on the frequency of the pulse train calculates the current position and the time span until the new end position. By applying this algorithm incurs an error every time a new position is calculated, since the algorithm does not take into account the time elapsed while the calculation is in process. This error, although it is minimal due to the processing speed of today's computers, is cumulative and when high frequencies are generated, will notably affect the accuracy of the slider.

There are several methods to correct this error, and the student is encouraged to explore the options and experiment with the results.

## D. Practice 04 – Speed control

The latter practice is intended to demonstrate the capabilities of closed loop control in the system, using as feedback the encoder sensor. This is used to measure the rotational speed of the servomotor and make the necessary adjustments to get the set speed.

Fig. 7. Frontal Panel – Speed Control

For the closed loop proportional control has been established which can be modified during program execution allowing to experiment with this type of control and experimentally observe the effects of this control over the output of our system is used.

# XI. CONCLUSIONS

- It has been determined that the maximum speed under load is 1500 RPM, a higher speed for a prolonged period of time can cause damage to the bearings of the slider.
- A system has been design that can be used by a wide range of students, it is not strictly necessary to have advanced knowledge in servomechanisms.
- Libraries were created in the development environment that allows an easy programming of the slider so that it adjust to the different practices of the slider.
- A robust design was achieved suitable to withstand potential abuse by students in their experiments.
- The module has implemented security measures that prevent the collision of the work table with the ends of the slider. In addition to a emergency stop button if needed.

# XII. Sugerencias

- Observe all safety precautions when operating the module to ensure long service life.
- Implementation of grounding for all lab computers electronics and mechatronics is suggested.
- Programming of both the library functions in LabVIEW as the microcontroller firmware are open source, study and improvement of algorithms implemented in the module is suggested.
- The module can be controlled from Matlab, implement control loops in this program is suggested as a practical example of its programmability.
- The slide table is capable of driving different types of additional mechanisms, the assembly of a robotic arm that allows the manipulation of objects is suggested.

# references

[16] Beer, F., & Johnston, R. (2010). MECÁNICA VECTORIAL PARA INGENIEROS. México: McGraw Hill.
[17] Sharp, R. (2008). Principles of Protocol Design. Kongens Lyngby: Springer.
[18] Blanding, D. L. (1995). Machine Design Using Kinematics Processing. New York: The American Socierty of Mechanical Engineers.
[19] NSK Corporation. (2005). What is a ball screw? Franklin.
[20] Scolum, A. H. (1992). Precision machine design. New Jersey: Prentice-Hall, Inc.
[21] GSK CNC Equipment Co. (2007). DA98D Digital AC Servo Drive Unit. Guanzhou.
[22] Hihglights. (2011). CONVERSIÓN DE SEÑAL DE ENCODER DE CUADRATURA . Cuenca, Ecuador.
[23] León Aguirre, A., & Tapia Vaca, J. (2009). Sincronismo y supervisión de posición y velocidad de un motor trifásico asíncrono con un sistema de encoders maestro-esclavo para aplicaciones de control de ejes. Latacunga: Escuela Politécnica del Ejercito.
[24] SKF Group. (20 de Enero de 2014). www.skf.com. Obtenido de http://www.skf.com/binary/12-55835/SKF4182_EN_Linear-ball-bearings.pdf
[25] THK. (2010). Guide Ball Bushing / Linear Bushing. Agoura Hills: THK.
[26] Hohner Corporation. (20 de Enero de 2014). www.encoderonline.com. Obtenido de http://www.encoderonline.com/Devicenet/Data-Sheets/Incremental/Data-33.htm
[27] Márquez Días, J., Pardo Sánchez, K., & Pizarro Valencia, S. (10 de Enero de 2014). http://rcientificas.uninorte.edu.co/. Obtenido de http://rcientificas.uninorte.edu.co/index.php/ingenieria/article/view/2272/1484
[28] Microsoft. (24 de 11 de 2013). http://technet.microsoft.com/. Obtenido de http://technet.microsoft.com/en-us/library/cc759499(v=ws.10)
[29] Zuñiga Tufiño, M. A. (2008). ESTUDIO DISEÑO Y SIMULACIÓN DE UN SISTEMA DE. Quito: ESCUELA POLITECNICA NACIONAL.
[30] Aerotech. (20 de Enero de 2014). www.aerotech.com. Obtenido de http://www.aerotech.com/media/247221/section16_motor%20selection%20and%20sizing.pdf

Autor

Ernesto Palacios Merino,

Born in Ecuador, in the city of Loja, he is a mechatronics student in the “Universidad Técnica del Norte” university.

He is currently employed in Kradac, in the robotics department.

[^1]
[^2]

1 Universidad Técnica del Norte. Palacios. Deslizador Lineal UTN.

7 Universidad Técnica del Norte. Palacios. Deslizador Lineal UTN.

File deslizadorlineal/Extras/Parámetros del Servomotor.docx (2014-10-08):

Parámetros de Velocidad:

PA Descripción Valor Iniciar

4 Modo de control 0

0 Control de posición

1 Control de velocidad
2 Modo de Prueba
3 Modo de control JOG
4 Ajuste de encoder a zero.
5 Lazo Abierto.

Parámetros de Velocidad:

PA Descripción Valor Iniciar

4 Modo de control 0

43 La velocidad es interna o analogica

CONECTOR UNO - CN1

N° PIN | Nombre | Función
38 | COM+ | Pin positivo para la entrada al Servo
23 | SON | Servo On, Enciende, bloquea al servomotor
30 | PULS+ | Tren de pulsos. Pin positivo
15 | PULS- | Tren de pulsos. Pin Negativo (GND)
29 | SIGN+ | Dirección. Pin positivo
14 | SIGN- | Dirección. Pin Negativo
5 | ALM | Señal de alarma (salida del driver)
33 | DGN | Digital GND. Tierra para la salida de la alarma
17 | VCMD | Entrada analógica +/- 10V
1 | AGND | Tierra analógica para VCMD

[38] COM+ Pin positivo de la fuente.

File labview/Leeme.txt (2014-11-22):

Aqui se guardaran los documentos del API para LabVIEW

Se dividen en dos categorías:

   -  HTTP      (Comunicación de red)
   -  Serial    (Comunicación serial)

Dentro de la carpeta 'librerias' se encuentran las sburutinas necesarias para que funcione correctamente la comunicacion de red con el microcontrolador.

La carpeta 'Practicas' contiene las Practicas desarrolladas para el deslizador.

La carpeta 'Pruebas' contiene programas útiles para probar las comunicación con el microcontrolador y servomotor.

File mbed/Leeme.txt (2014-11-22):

--------------------------------------------
Codigo Fuente Microcontrolador <mbed>

Autor: Ernesto Palacios
--------------------------------------------

Esta carpeta contiene el código fuente y los archivos binarios
necesarios para el micro controlador ARM-CortexM3-LPC1768 dentro
de la plataforma mbed [http//:mbed.org].

Este código puede ser compilado en linea a través del compilador 
en el servidor del sitio  [http//:developer.mbed.org].

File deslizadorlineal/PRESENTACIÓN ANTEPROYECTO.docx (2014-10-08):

# Universidad Técnica del Norte

FACULTAD DE INGENIERÍA EN CIENCIAS APLICADAS

CARRERA DE INGENIERÍA EN MECATRÓNICA

# ANTEPROYECTO DE TRABAJO DE GRADO

# DATOS GENERALES

# 1. TEMA:

# Sistema modular para prácticas de servomecanismos y control mediante deslizador lineal e Interfaz con LabVIEW.

# 2. ÁREA / LÍNEA DE INVESTIGACIÓN:

# Mecánica, Automatización, Control.

# 3. ENTIDAD QUE AUSPICIA:

# Autofinanciado.

# 4. DIRECTOR:

# Ing. Javier Rosero

# 5. AUTOR: Ernesto Vladimir Palacios Merino

# DIRECCIÓN: Maldonado 14-86 y Obispo Mosquera

# TELÉFONO: 080526156

# CORREO ELECTRÓNICO: mecatronica.mid@gmail.com

# LUGAR DE TRABAJO:

# TELÉFONO TRABAJO:

# DIRECCIÓN DE TRABAJO:

# 6. DURACIÓN (Estimado):

# 6 meses

# 7. INVESTIGACIÓN: Nueva (x) Continuación ( )

# 8. PRESUPUESTO (estimado): USD $ 800

# PARA USO DEL CONSEJO ACADÉMICO

FECHA DE ENTREGA: | FECHA DE REVISIÓN:
APROBADO: SI ( ) NO ( ) | FECHA DE APROBACIÓN:

# OBSERVACIONES:

# Universidad Técnica del Norte

FACULTAD DE INGENIERÍA EN CIENCIAS APLICADAS

CARRERA DE INGENIERÍA EN MECATRÓNICA

PLAN DEL PROYECTO DE TITULACIÓN

Propuesto por: Ernesto Vladimir Palacios Merino | Áreas Técnicas del Tema: - Mecanismos - Automatización - Control
Director sugerido: Ing. Xavier Rosero | Fecha: Ibarra, 03 de febrero de 2012

1. Tema

Sistema modular para prácticas de servomecanismos y control mediante deslizador lineal e Interfaz con LabVIEW.

2. Problema

La Universidad Técnica del Norte posee muchos de los materiales necesarios para la realización de prácticas en el área de mecatrónica pero para la materia de servomecanismos aún es necesario ampliar la funcionalidad de los elementos que actualmente están a la disposición de los estudiantes.

En la actualidad el laboratorio cuenta con varios sistemas “entrenadores” los cuales hacen que la tarea del estudiante se vuelva más simple y rápida. Existen módulos para realizar prácticas de neumática, de control de temperatura, y automatización, pero no existe una solución similar para servomecanismos. El módulo existente de servomecanismos es restringido y limitado, restringido porque para su control está definido el uso de un solo PLC y limitado porque no cuenta con un sistema mecánico que demuestre su funcionalidad.

Por tal motivo es necesario construir un elemento mecánico que complemente el módulo de servomecanismos, y dotarlo con un controlador que permita un manejo más sencillo del motor y mayor flexibilidad a la hora de controlarlo.

3. Objetivos

# Objetivo General

Construir un sistema modular para desarrollar prácticas de laboratorio en la Carrera de Ingeniería en Mecatrónica, en la Universidad Técnica del Norte, para mejorar la funcionalidad del módulo de servomotores.

# Objetivos Específicos

    - Determinar la implementación más adecuada para el mecanismo del deslizador
    - Diseñar y construir el deslizador lineal.
    - Diseñar e implementar el controlador microprocesado del servomotor.
    - Diseñar e implementar la interfaz de programación en LabVIEW.
    - Elaborar manuales de prácticas y mantenimiento.
4. Alcance

La longitud del deslizador será de aproximadamente ochenta centímetros. El sistema está diseñado para ser controlado desde el entorno de programación de LabVIEW. Para ello se escribirán librerías que proporcionen la interfaz de comunicación con el microcontrolador el cual controlará el servomotor.

El módulo contará con dos tipos de comunicación para su control, uno serial y uno ethernet. El controlador se implementará con un microcontrolador ARM mbed. La comunicación serial se diseñará para comunicarse con otros microcontroladores, u otros lenguajes de programación.

Se proveerá de tres niveles para la interfaz programador - aplicación: bajo nivel, nivel medio y nivel alto. El nivel bajo controlará directamente las variables del microcontrolador, la salida del tren de pulsos, y la entrada de cuadratura, el nivel medio controlará directamente al motor, velocidad de rotación y posición relativa, finalmente el alto nivel actuará sobre el deslizador, velocidad lineal y posición relativa de la base del deslizador. Esto dotará de mayor flexibilidad a la programación del módulo, dependiendo del tipo de práctica que se desee realizar.

Se utilizará un servomotor y un driver, un encoder absoluto acoplado al eje rotacional del motor, el software LabVIEW y la red local del laboratorio, todos estos elementos ya se encuentran en el laboratorio de mecatrónica para su utilización.

5. Justificación

La complementación de los conocimientos teóricos con los prácticos es de vital importancia para la carrera de mecatrónica, debido a que el mercado profesional de un ingeniero en mecatrónica cada día se vuelve más exigente en lo que se refiere a práctica en campo. Es por eso importante dotar nuestros laboratorios de los elementos necesarios para llevar a cabo estas prácticas.

El laboratorio de mecatrónica cuenta con módulos CNC y cuatro servo motores, para realizar las prácticas de servomecanismos, pero no cuenta con ningún sistema actuador, además para el control de éstos motores se tiene únicamente como controlador el PLC Siemens S7-200, por lo que la adición de un sistema que permita un control más flexible beneficiará al estudiante al momento de realizar sus prácticas.

Por tal razón se propone la construcción de un sistema actuador mediante un deslizador lineal, el cual cuente con un interfaz de programación en LabVIEW, la utilización de un micro controlador en lugar del controlador lógico programable, el cual servirá para realizar diversas prácticas tanto de servomecanismos como de control.

6. Contexto

No existen temas afines actualmente en la universidad.

7. Contenidos

CAPITULO I. ANTECEDENTES

1.1 Introducción

1.2 El microcontrolador ARM mbed

1.3 El servomotor

1.4 Protocolo de comunicación ethernet

1.5 Programación gráfica en LabVIEW

CAPITULO II. ARQUITECTURA DEL SISTEMA

2.1 Descripción general

2.2 Concepción a bloques

2.3 Determinación de subsistemas

2.3.1 Estructura del deslizador

2.3.2 Controlador microprocesado

2.3.3 API del controlador en LabVIEW

2.3.4 Respuesta

CAPITULO III. DISEÑO DEL SISTEMA

3.1 Estructura del deslizador

3.1.1 Sistema mecánico

3.1.2 Deslizador

3.2 Controlador microprocesado

3.2.1 Diagrama de control

3.2.2 Esquema del circuito

3.2.3 Programación del microprocesador

3.3 API para el control y monitoreo en LabVIEW

3.3.1 API de bajo nivel

3.3.2 API de nivel medio

3.3.3 API de alto nivel

3.4 Respuesta

3.4.1 Motor

3.4.2 Driver

CAPITULO IV. IMPLEMENTACIÓN Y PRUEBAS

4.1 Implementación física del módulo

4.2 Calibración del módulo

4.3 Pruebas de funcionamiento

CONCLUSIONES

RECOMENDACIONES

ANEXOS

Manual de operación del módulo

Documentación de la interfaz de programación

Manual de las prácticas a desarrollarse con el módulo

Manual de mantenimiento del módulo.

8. Cronograma de Actividades

Actividad | Mes 1 | Mes 2 | Mes 3 | Mes 4 | Mes 5 | Mes 6
Presentación y Aprobación del plan | x
Diseño y Construcción del Deslizador | | x | x
Diseño y Construcción del Controlador | | x | x
Programación en LabVIEW | | | x | x | x
Implementación | | | | x | x
Pruebas de Funcionamiento | | | | x | x
Conclusiones y Recomendaciones | | | | | x
Entrega de Borradores | | | | | x | x

9. Presupuesto
      a) Materiales y elementos de estudio:

Nº | Descripción | Subtotal
1 | Internet | 100
2 | Adquisición de Libros y revistas | 50
TOTAL (1) | | 150

      b) Diseño y construcción mecánica:

Nº | Descripción | Subtotal
1 | Estructura del deslizador | 500
TOTAL | | 500

      c) Diseño e implementación del sistema eléctrico y electrónico:

Nº | Descripción | Subtotal
1 | Material eléctrico y electrónico | 50
2 | Microcontrolador | 100
TOTAL (2) | | 150

Nº | Descripción | Subtotal
1 | Material Elementos de estudio | 150
2 | Sistema mecánico | 500
3 | Sistema electrónico | 150
TOTAL (3) | | 800

10. Bibliografía

Libros:

1. GSK. Manual de usuario, Driver DA98D. GSK CNC Equipment.
2. Mott, R.L., (2006). Diseño de Elementos de Máquinas. Prentice Hall. (4ta Edicion). Mexico
3. Yiu Joseph (2008). The Definitive Guide to the ARM Cortex-M. Prentice Hall. (2da Edición ). Reino Unido
4. Dam Bert (2011). ARM Microcontrollers 1. Elektor. (1era Edición). Reino Unido
5. Savitch Walter (2011). Absolute C++. McGraw Hill. (5ta Edición). Estados Unidos

Publicaciones en línea:

1. Mbed, (2011), Interfaz con LabVIEW. Recuperado de: http://mbed.org/cookbook/Interfacing-with-LabVIEW/
2. Mbed, (2011), Tour. Recuperado de:

http://mbed.org/handbook/Tour

3. HIVIMAR, Rodamientos y afines. Recuperado de http://www.hivimar.com/productos/rodamientos-y-afines/

DIRECTOR ESTUDIANTE

GUÍA PARA PREPARAR EL PLAN DEL PROYECTO DE TRABAJO DE GRADO

##### TEMA O TÍTULO

El título del proyecto debe expresar en forma clara, concisa y univoca el objeto del mismo. Se lo debe especificar mediante una frase que resuma el proceso y/o el trabajo a realizarse en el proyecto.

##### PROBLEMA

Es la descripción del problema que se quiere solucionar con el trabajo de grado. Debe constar de: un párrafo con antecedentes, un párrafo con situación actual y un párrafo con prospectiva, Un párrafo final a modo de resumen de los tres anteriores.

##### OBJETIVOS

Es la descripción de lo que se pretende conseguir con el Proyecto. Podrá contener además la naturaleza del equipo, sistema, instalación o construcción que se va a proyectar.

Se deben plantear el objetivo general y los objetivos específicos.

Objetivo general.

El objetivo general debe ser CONCRETO, MEDIBLE, REALIZABLE, REALISTA y DELIMITADO EN TIEMPO.

Objetivos específicos.

Los específicos se refieren a situaciones particulares que inciden en el objetivo general.

Al redactar los objetivos de la investigación deben utilizarse verbos en infinitivo.

Otro aspecto muy importante al momento de plantear los objetivos de la investigación es utilizar verbos que puedan lograrse o alcanzarse durante el desarrollo de la investigación. A continuación algunos posibles verbos.

Determinar Diseñar Elaborar

Verificar Emplear Corroborar

Definir Mejorar Plantear

Seleccionar Calcular Evaluar

Optimizar Analizar Proponer

Comprobar Producir Resolver

En la medida de lo posible utilizar el siguiente esquema.

Verbo+objeto de investigación + sujetos + contexto + finalidad u otro objetivo/relación

Ej.

Construir un sistema tecnológico para desarrollar prácticas de laboratorio de hidrodinámica, en la carrera de Ingeniería en Mecatrónica de la UTN, para mejorar el aprendizaje de la materia Mecánica de fluidos.

#### ALCANCE

Describe los límites en los que se mueve el Trabajo de grado, y entre los que es válido. Delimita además la profundidad del trabajo. El alcance debe tener relación con el objetivo, lo debe detallar y permitir su cuantificación.

#### JUSTIFICACIÓN

Toda investigación está orientada a la resolución de algún problema; por consiguiente, es necesario justificar, o exponer los motivos que merecen la investigación. Así mismo, debe determinarse su dimensión para conocer su viabilidad.

Son las razones por las cuales se plantea el proyecto y se le otorga validez. El proyecto debe tener una o varios tipos de justificaciones que deben ser especificadas. Justificación Tecnológica.-

Se considera que una investigación tiene justificación práctica o tecnológica cuando su desarrollo ayuda a resolver un problema o, por lo menos, propone estrategias que de aplicarlas contribuirían a resolverlo, se debe dar énfasis en el impacto económico, social y/o ambiental que tendrá la realización del trabajo de investigación.

Justificación teórica.-

Existe una justificación teórica cuando el propósito del estudio es generar reflexión y debate académico sobre el conocimiento existente, confrontar una teoría, contrastar resultados o hacer epistemología del conocimiento existente.

Justificación Metodológica.-

La justificación metodología del estudio se da cuando el proyecto por realizar propone un nuevo método o una nueva estrategia para generar conocimiento válido y confiable.

#### CONTEXTO

Se debe hacer referencia a otros proyectos o estudios similares ya realizados y resaltar las aportaciones más importantes que se van a lograr con el proyecto planteado.

#### CONTENIDOS

Es una guía para la preparación del trabajo escrito, del contenido mismo del proyecto. En el formulario para la presentación del Plan del Proyecto, se exige consignar al menos los capítulos que contendrá el reporte escrito, los que deben tener íntima relación con los objetivos específicos.

Cualquier cambio posterior en el temario, que no afecte los objetivos y alcance del proyecto, deberá comunicarse por escrito y recibir la aprobación del Coordinador de Carrera

#### CRONOGRAMA DE ACTIVIDADES

Se deben señalar las diferentes etapas o actividades del proyecto y el tiempo estimado para cada una de ellas. Mediante la gráfica de Gantt se establece una relación entre actividad y tiempo de ejecución.

#### PRESUPUESTO

Detallar el presupuesto a ser utilizado y de existir el financiamiento explicar si es personal o de alguna institución o empresa auspiciante. Anexar carta de auspicio de la entidad auspiciante.

#### BIBLIOGRAFÍA

La descripción debe realizarse utilizando formato APA 6ͭ ͣ edición.

## LIBROS

FORMATO GENERAL

Apellido, N., Apellido, N.(año). Título del libro. Ciudad: Editorial.

Ej.

Gillis, M., Perkins, D., Roemer, M., & Snodgrass, D. (1987). Economics of development (2nd ed.). New York: WW Norton & Company.

### PUBLICACIONES EN LINEA

Artículo electrónico con DOI (Digital Object identifier)

FORMATO GENERAL

Autor, A. A. (fecha de publicación). Título del artículo. Título de la publicación periódica, volumen (número), número de páginas. doi: xx.xxxxxxx

Ej.

Herbst-Damm, K. L., & Kulik, J. A. (2005). Volunteer support, marital status, and the

survival times of terminally ill patients. Health Psychology, 24, 225-229. doi:

10.1037/0278-6133.24.2.225

Artículo electrónico sin DOI

FORMATO GENERAL

Autor, A. A. (fecha de publicación). Título del artículo. Título de la publicación periódica, volumen (número), número de páginas. Recuperado de URL

Ej.

Sillick, T. J., & Schutte, N. S. (2006). Emotional intelligence and self-esteem mediate

between perceived early parental love and adult happiness. Applied Psychology,

2(2), 38-48. Recuperado de http://ojs.lib.swin.edu.au/index.php/ejap

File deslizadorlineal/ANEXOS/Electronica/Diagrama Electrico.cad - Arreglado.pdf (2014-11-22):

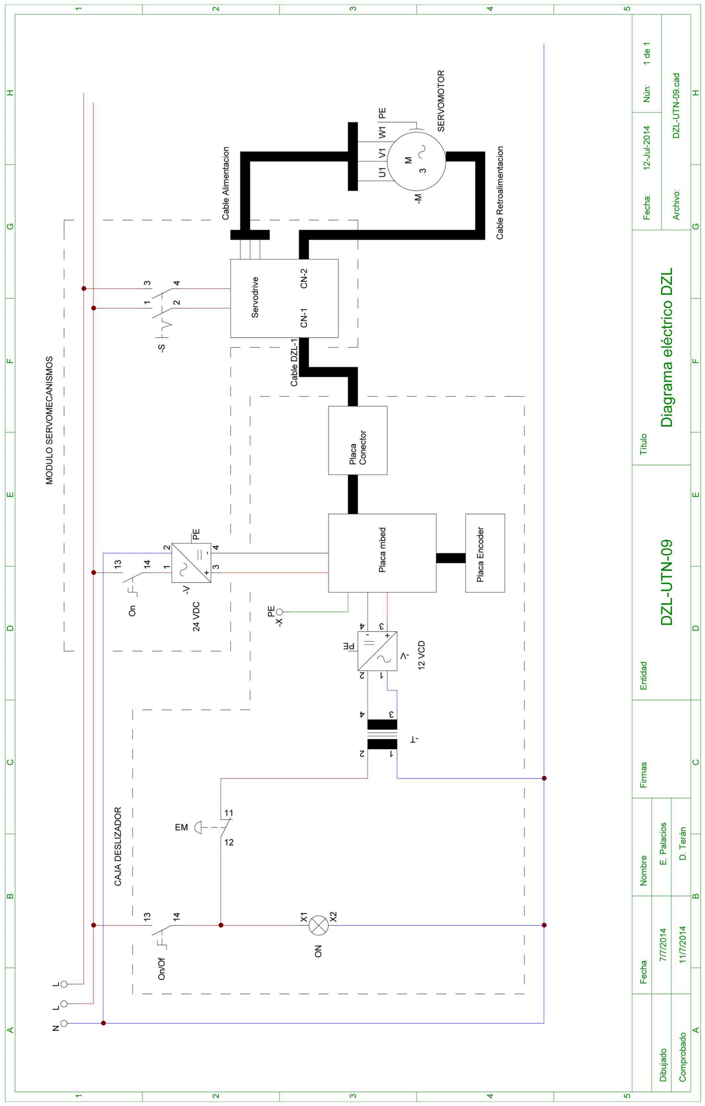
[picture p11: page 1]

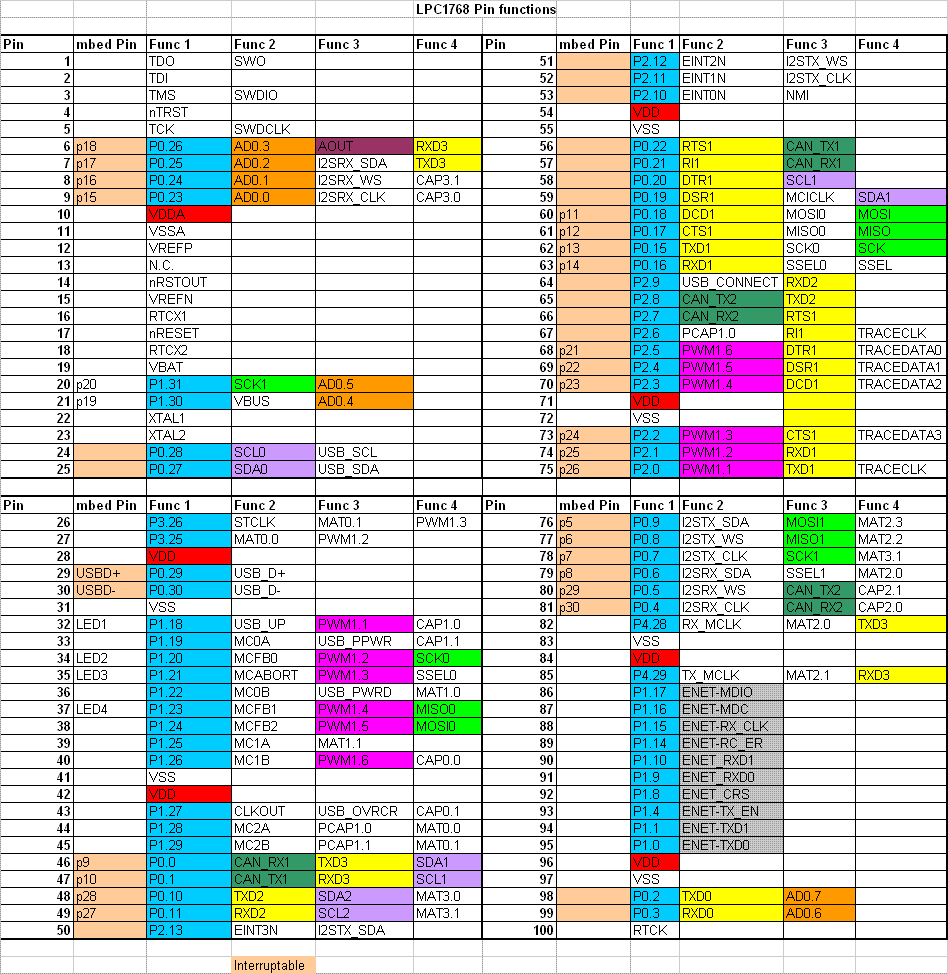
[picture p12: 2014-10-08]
deslizadorlineal/ANEXOS/Electronica/lpc1768_pin_functions.gif

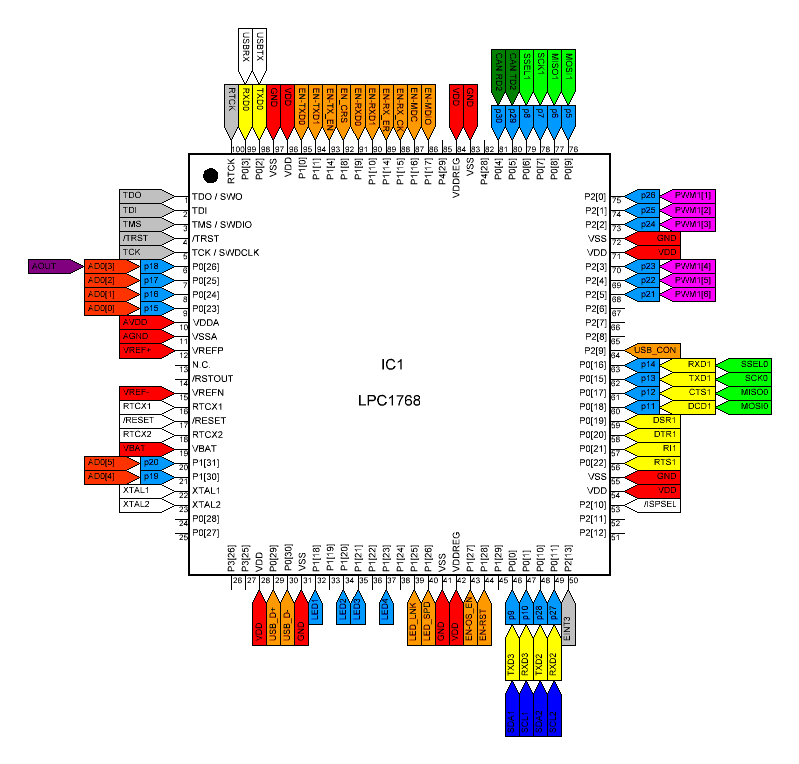
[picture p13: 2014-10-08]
deslizadorlineal/ANEXOS/Electronica/lpc1768_mbed_pinout.gif

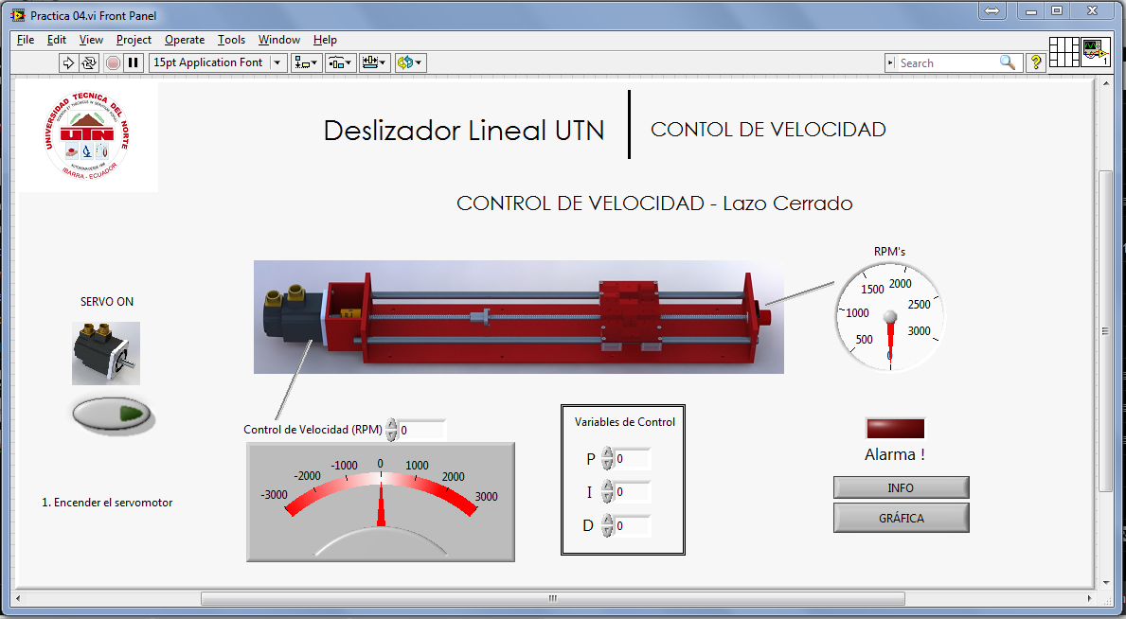
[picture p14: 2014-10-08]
deslizador/SolidW_Final/Renders/Programa/Practica 04.png

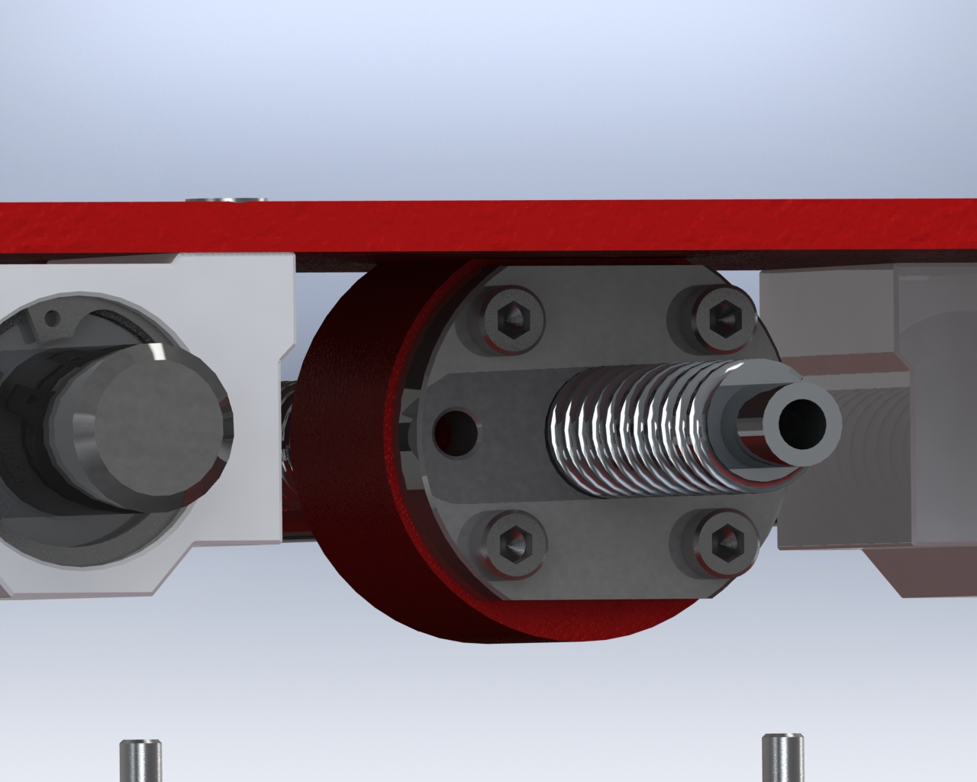
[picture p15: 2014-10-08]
deslizador/SolidW_Final/Renders/nuez de tornillo.JPG

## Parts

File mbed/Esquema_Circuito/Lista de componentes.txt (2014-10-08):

Componentes placa mbed_v2

LISTA COMPLETA

COMPONENTES IMPORTANTES:

N°      Nombre    	Descripcion

1	AD620N		Amplificador Operacional
1	MAX232		Conversor RS-232 - TTL
1	DIP Switch 3	Switcher de tres bits DIP

5      2k2 R		Resistencias de 2200 ohm 1/4 watt
5      3k3 R		Resistencias de 3300 ohm 1/4 watt
5 	470k R		Resistencias de 470k ohm 1/4 watt
5	220 R		Resistencias 220 ohm 1/2 watt
5      10k R		Resistencias de 10K ohm 1/4 watt

10	Cap 0.1uF 	Capacitor cerámico [104]
5	Cap 1uF		Capacitor Electrolitico.

2	20pin x 2		Headers hembra de dos filas 20 pines
2	Conector Ethernet  con aislamiento magnetico.
2	Puente de diodos de 1A

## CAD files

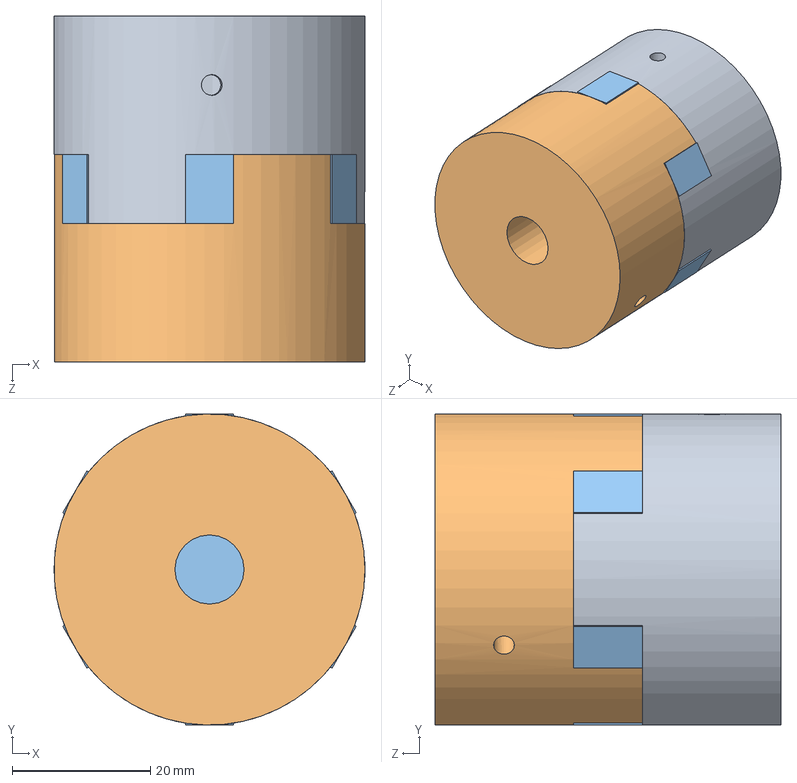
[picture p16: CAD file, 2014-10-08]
deslizador/SolidW_Final/Lovejoy coupling.SLDASM
45.0 x 45.0 x 50.0 mm
Lovejoy motor
Lovejoy 2
lovejoy_spacer

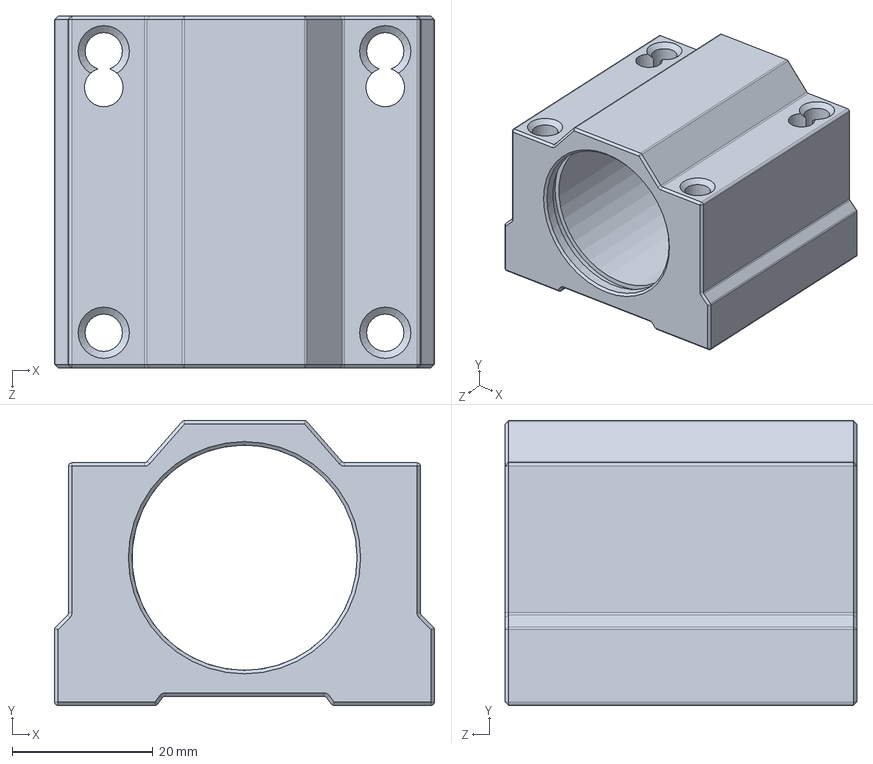
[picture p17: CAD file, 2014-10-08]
deslizador/SolidW_Final/linear-bearing-scs-20uu-1.snapshot.1/bearing.SLDPRT
54.0 x 40.5 x 50.0 mm

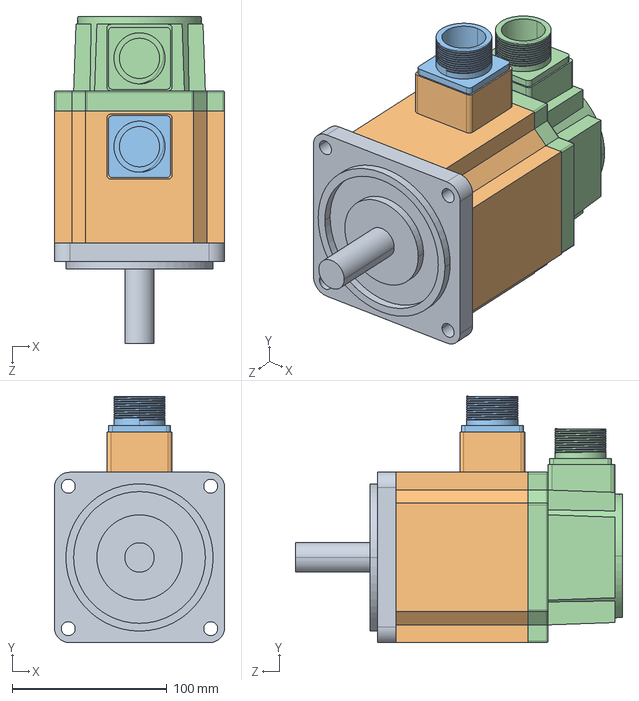
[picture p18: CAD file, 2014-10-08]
deslizador/SolidW_Final/Servo_110SJT-M020E.STEP
110.0 x 159.0 x 211.0 mm

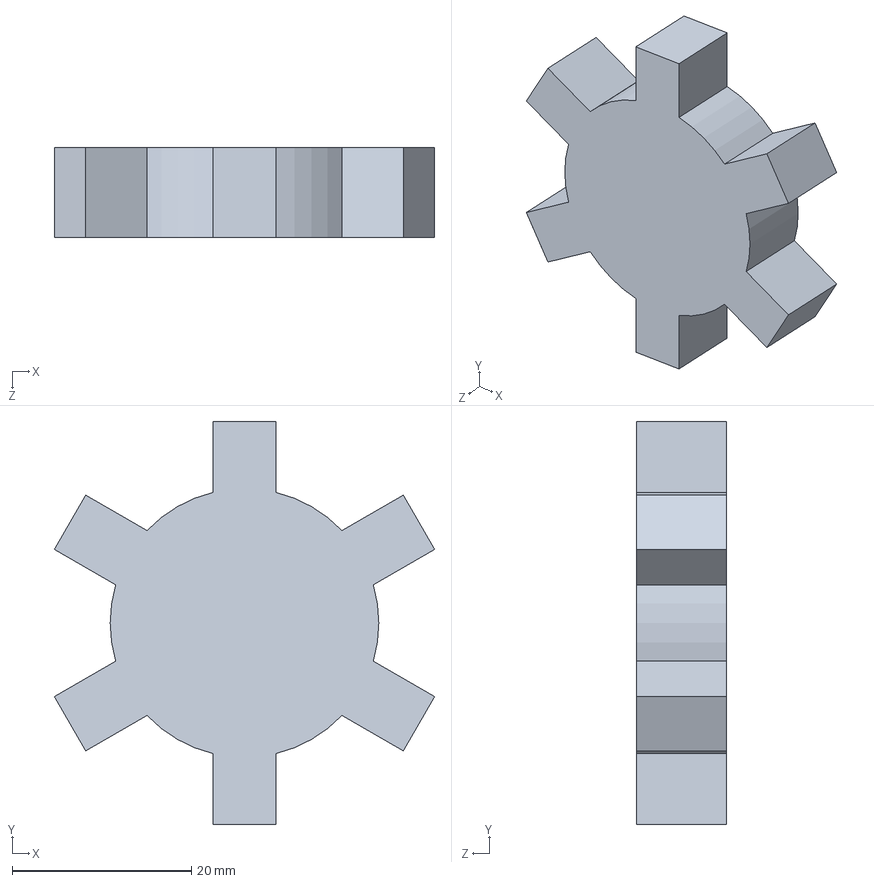
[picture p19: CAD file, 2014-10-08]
deslizador/SolidW_Final/lovejoy_spacer.SLDPRT
42.5 x 45.0 x 10.0 mm

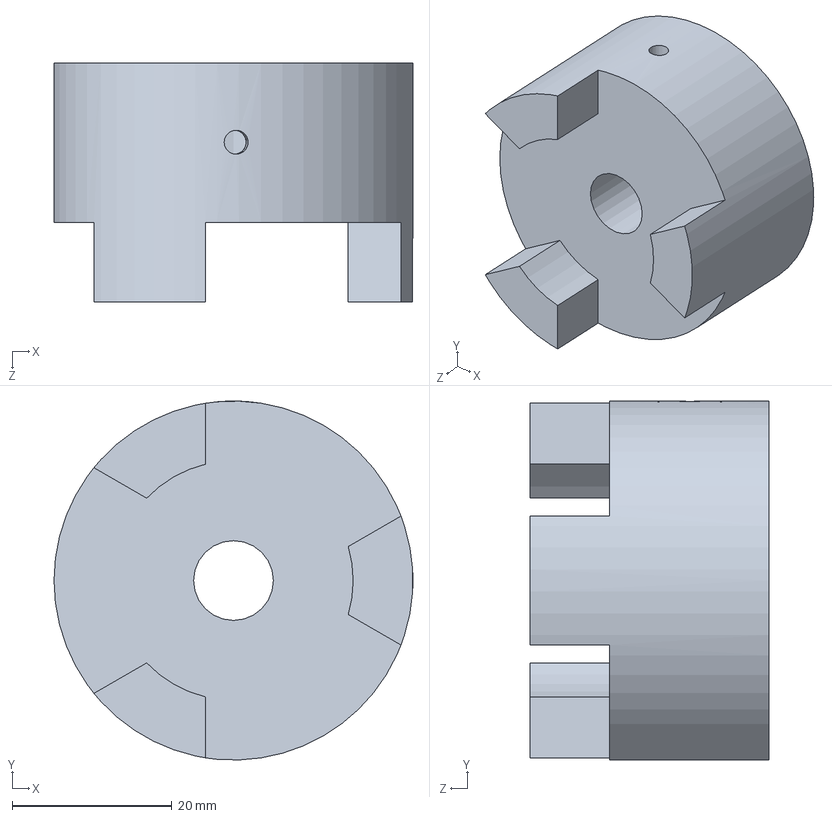
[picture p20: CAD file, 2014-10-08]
deslizador/SolidW_Final/Lovejoy 2.SLDPRT
45.0 x 45.0 x 30.0 mm

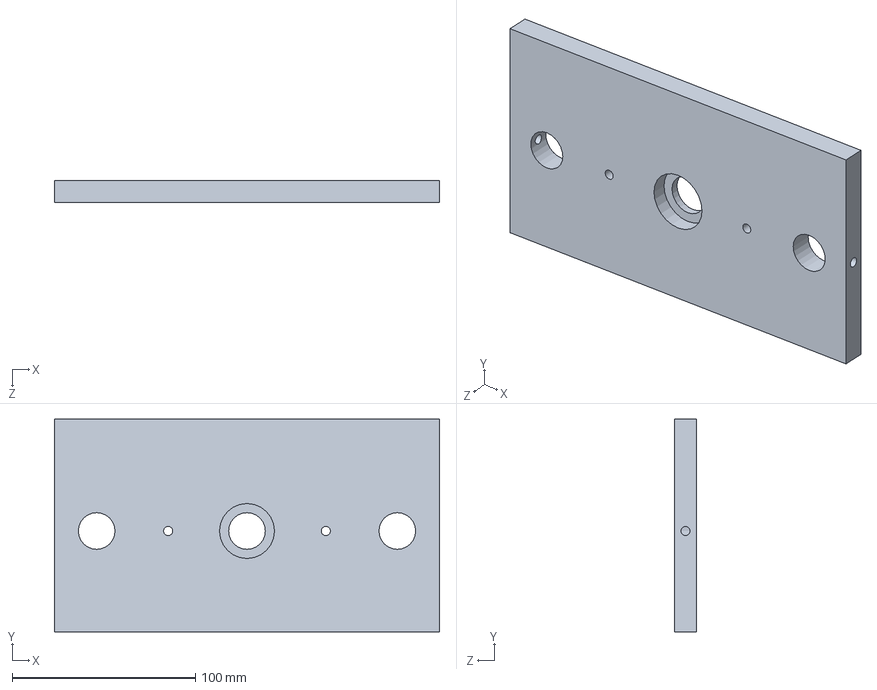
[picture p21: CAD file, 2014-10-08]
deslizador/SolidW_Final/Placa Encoder.SLDPRT
210.0 x 116.0 x 12.0 mm

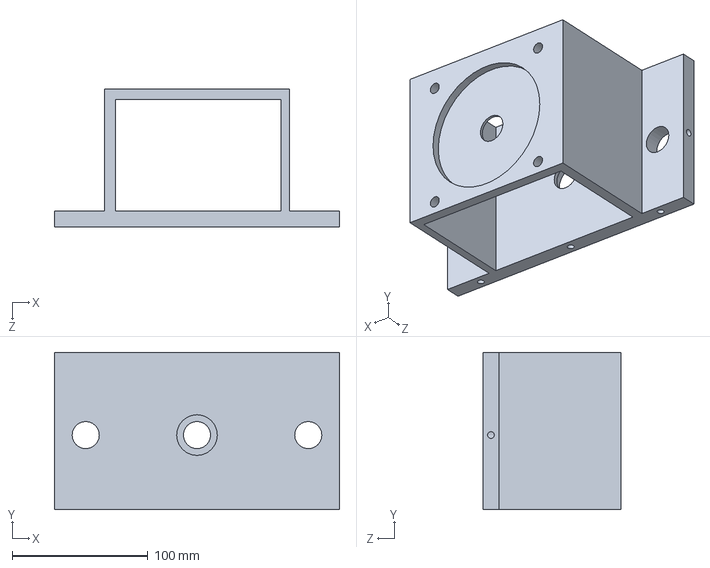
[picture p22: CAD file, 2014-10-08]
deslizador/SolidW_Final/Placa Motor.SLDPRT
210.0 x 116.0 x 102.0 mm

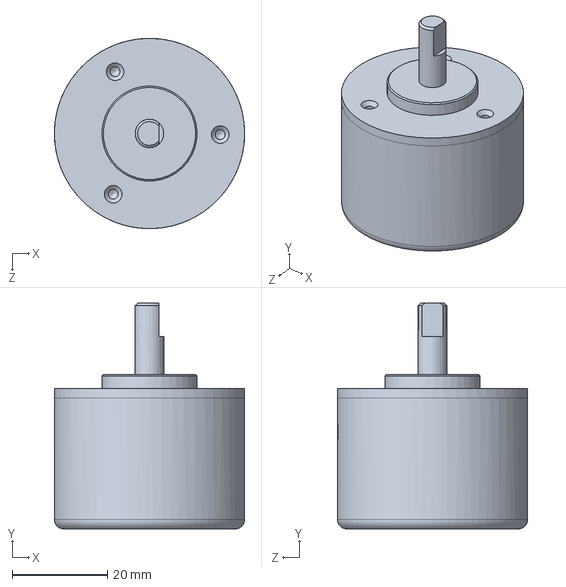
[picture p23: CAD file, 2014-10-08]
deslizador/SolidW_Final/Encoder_hohner.SLDPRT
40.0 x 47.5 x 40.0 mm

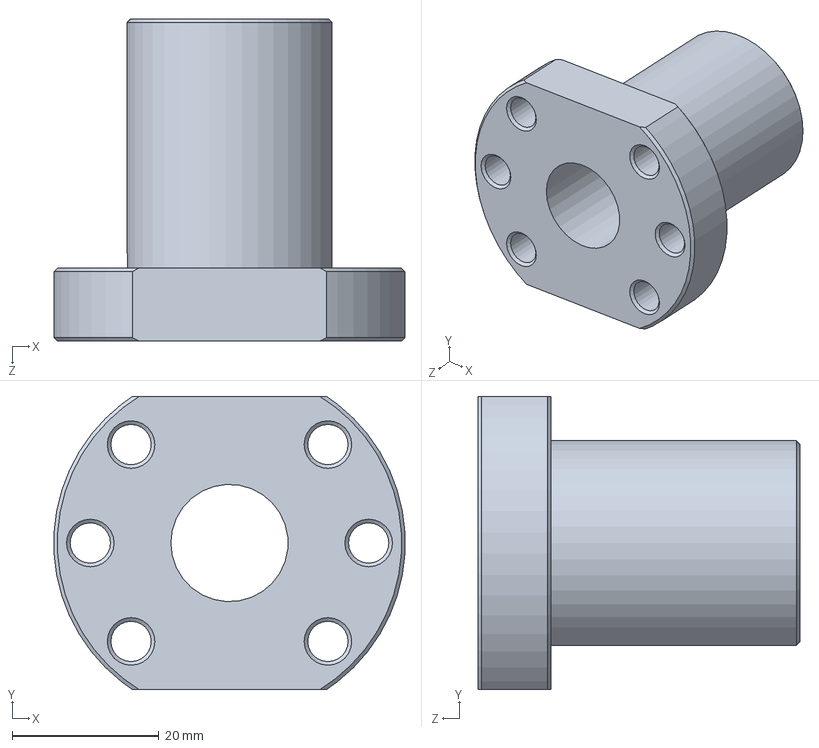
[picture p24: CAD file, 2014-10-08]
deslizador/SolidW_Final/nuez tornillo.SLDPRT
47.9 x 40.0 x 44.0 mm

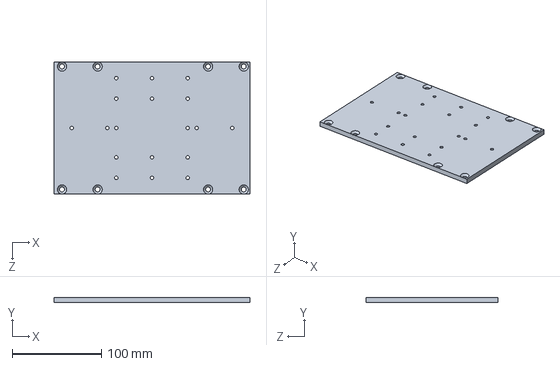
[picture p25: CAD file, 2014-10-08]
deslizador/SolidW_Final/Deslizador Base.SLDPRT
220.0 x 6.00 x 148.0 mm

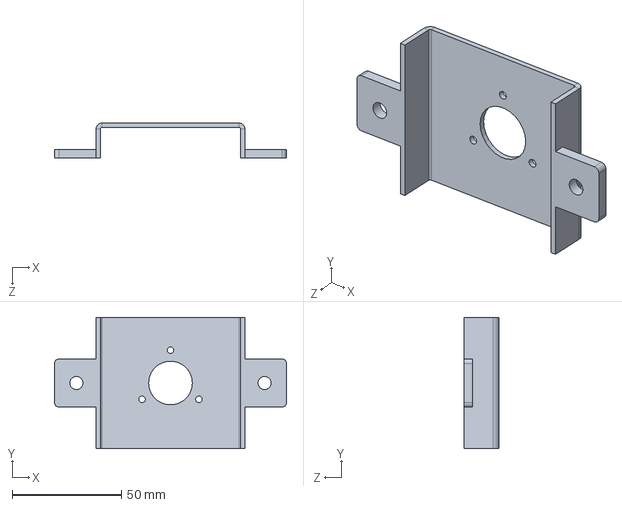
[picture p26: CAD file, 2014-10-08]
deslizador/SolidW_Final/Sujeta Encoder.SLDPRT
106.0 x 60.0 x 16.0 mm

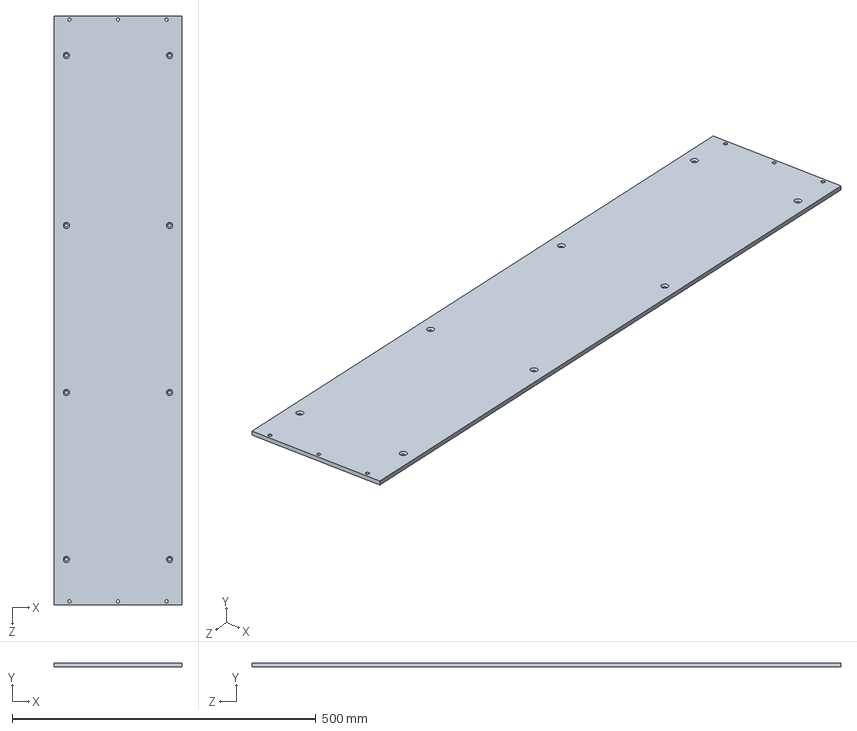
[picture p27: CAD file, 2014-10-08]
deslizador/SolidW_Final/Placa Base.SLDPRT
210.0 x 6.00 x 970.0 mm

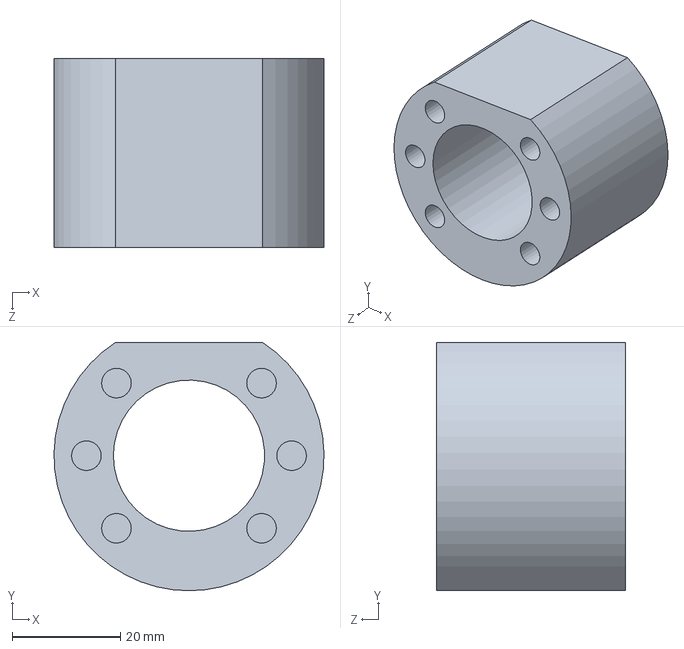
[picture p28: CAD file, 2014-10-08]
deslizador/SolidW_Final/Acople nuez.SLDPRT
50.0 x 46.0 x 35.0 mm

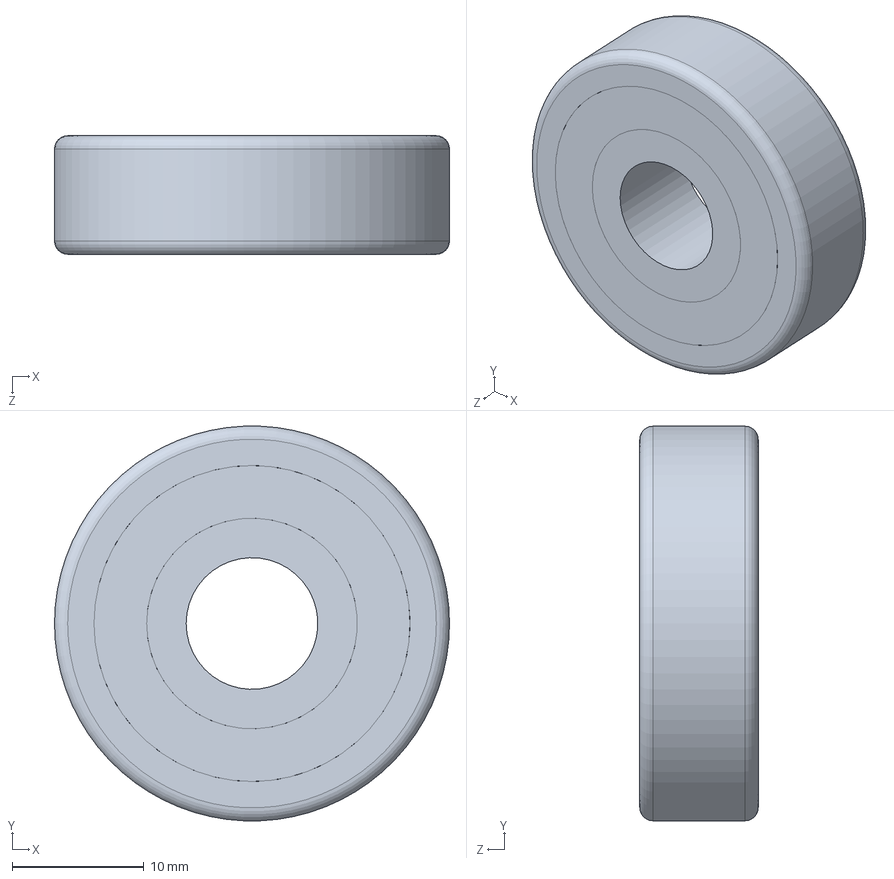
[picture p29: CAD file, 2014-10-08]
deslizador/SolidW_Final/Rodamiento_10mm.SLDPRT
30.0 x 30.0 x 9.00 mm

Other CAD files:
deslizador/SolidW_Final/Lovejoy motor.SLDPRT
deslizador/SolidW_Final/LoveJoy.SLDPRT
deslizador/SolidW_Final/socket-head-set-screws/SERIES 049 - SOCKET SET SCREWS.STEP
deslizador/SolidW_Final/SERIES 049 - SOCKET SET SCREWS.SLDPRT
deslizador/SolidW_Final/Servo_110SJT-M020E.SLDPRT
deslizador/SolidW_Final/Servo_110SJT-M020E.STL
deslizador/SolidW_Final/socket-head-set-screws/SERIES 049 - SOCKET SET SCREWS.SLDPRT

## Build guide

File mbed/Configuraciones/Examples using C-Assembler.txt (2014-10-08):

Examples using C/Assembler

void initTMR0(){

    // power up TIMER0 (PCONP[1])
    LPC_SC->PCONP |= 1 << 1; 

    // reset and set TIMER0 to timer mode
    LPC_TIM0->TCR = 0x2;  
    LPC_TIM0->CTCR = 0x0; 
    
    // set no prescaler
    LPC_TIM0->PR = 0;

    // calculate period (1 interrupt every mili-second)
    uint32_t period = SystemCoreClock / 4000; 

    // set match register and enable interrupt    
    LPC_TIM0->MR0 = period;
    LPC_TIM0->MCR |= 1 << 0;    // interrupt on match
    LPC_TIM0->MCR |= 1 << 1;    // reset on match

    // enable the vector in the interrupt controller
    NVIC_SetVector(TIMER0_IRQn, (uint32_t)&getAngle);
    NVIC_EnableIRQ(TIMER0_IRQn);

    // start the timer
    LPC_TIM0->TCR = 1;
}

void ISR_Serial(){
    char c = pc.getc();

    if( c = 'w')
       setPeriodUp();
    else if( c = 's')
       setPeriodDown();
    
    else if( c = 'z')
    {
        float newStep;
        pc.printf("\nIntroduce new step: ");
        pc.scanf( "%d", &newStep );
        setPeriodStep( newStep );
    }

}

pc.attach( &ISR_Serial );

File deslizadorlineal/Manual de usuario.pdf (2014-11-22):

# Deslizador Lineal UTN Manual de operación

### 1. Generalidades

El presente documento tiene la finalidad de ayudar al estudiante a conocer y

comprender el correcto manejo del sistema mecánico y electrónico del deslizador,

y los pasos que debe seguir para su correcto mantenimiento.

Este documento complementa y extiende lo visto en los capítulos dos y tres

del trabajo de grado que acompaña este anexo, para una comprensión completa

de lo aquí expuesto se recomienda la lectura de estos capítulos.

### 2. Armado y desarmado del módulo

La estructura del sistema mecánico se encuentra dividida en tres partes, se

tiene la estructura de soporte, luego tenemos la transmisión de potencia, y

finalmente el carro deslizador.

La estructura de soporte es fácilmente reconocible ya que se encuentra

pintada de rojo. Esta estructura se encuentra ensamblada mediante tornillos lo

que permite poder desarmarla y cambiar componentes de ser necesario.

Los elementos de transmisión de potencia son, el tornillo de bolas, el

matrimonio que acopla los ejes, y los rodamientos radiales que sostienen el

tornillo. Estos elementos son los encargados de transmitir la potencia al carro

deslizador.

El carro del deslizador se asienta sobre los rodamientos lineales, los cuales

se deslizan a lo largo de sus guías quienes son las encargadas de soportar el la

carga a la que se somete el deslizador.

El servomotor es el elemento actuador, se sujeta al tornillo a un extremo del

mismo mientras que en el extremo opuesto se encuentra conectado el encoder de

cuadratura.

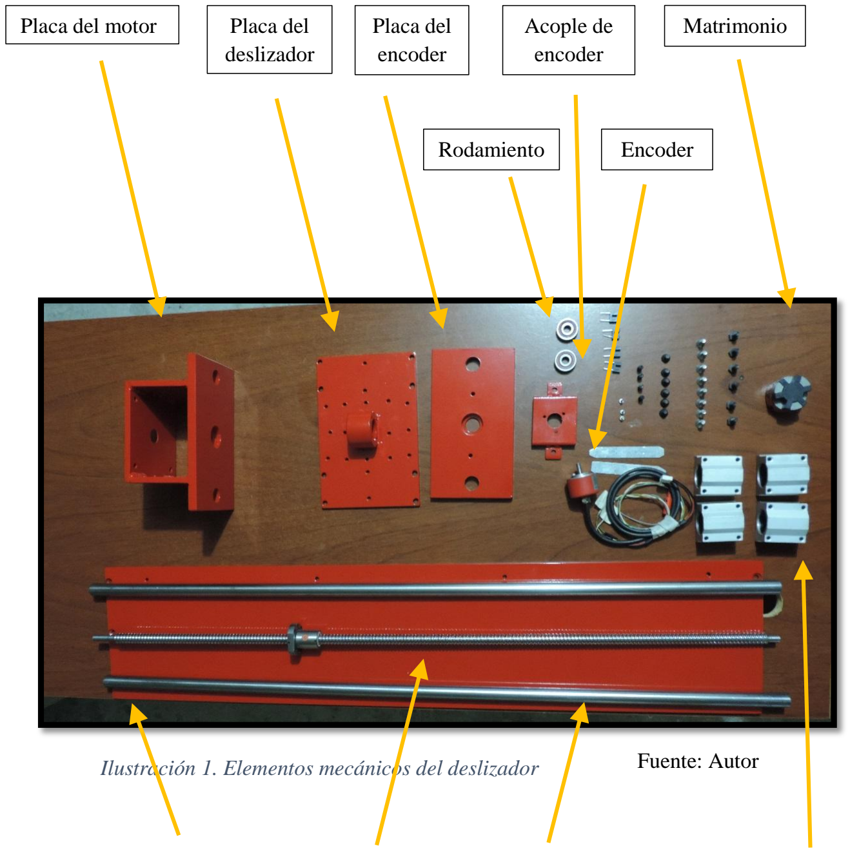
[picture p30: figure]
Placa del motor; Placa del; deslizador; Placa del encoder; Acople de encoder; Matrimonio; Rodamiento; Encoder; Fuente: Autor

Ilustración 1. Elementos mecánicos del deslizador

A continuación se explicara detalladamente cada uno de estos

componentes.

### 2.1. Estructura del deslizador

Las placas del deslizador cuentan en su centro con una abertura donde se

coloca el rodamiento radial que se sujetará al tornillo de bolas. En caso de ser

necesario se puede cambiar los mismos.

Placa base | Tornillo
de bolas
Guias | Rodamientos
Linelaes

Ilustración 2. Rodamiento radial

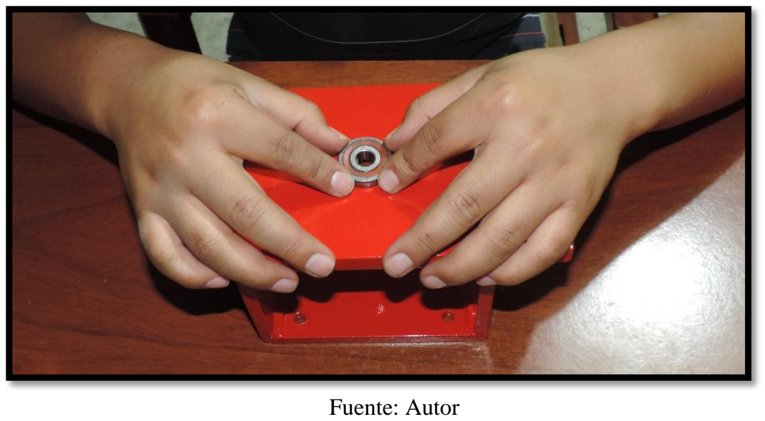
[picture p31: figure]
Fuente: Autor

Los rodamientos deben tener un diámetro interno de 10 mm y uno externo de

30 mm.

La base del deslizador es una placa de 970 x 210 x 6 milímetros, en sus

extremos cuenta con perforaciones que permiten sujetar la placa del encoder en

un extremo y la del motor en el otro.

Ilustración 3. Sujeción de la placa base

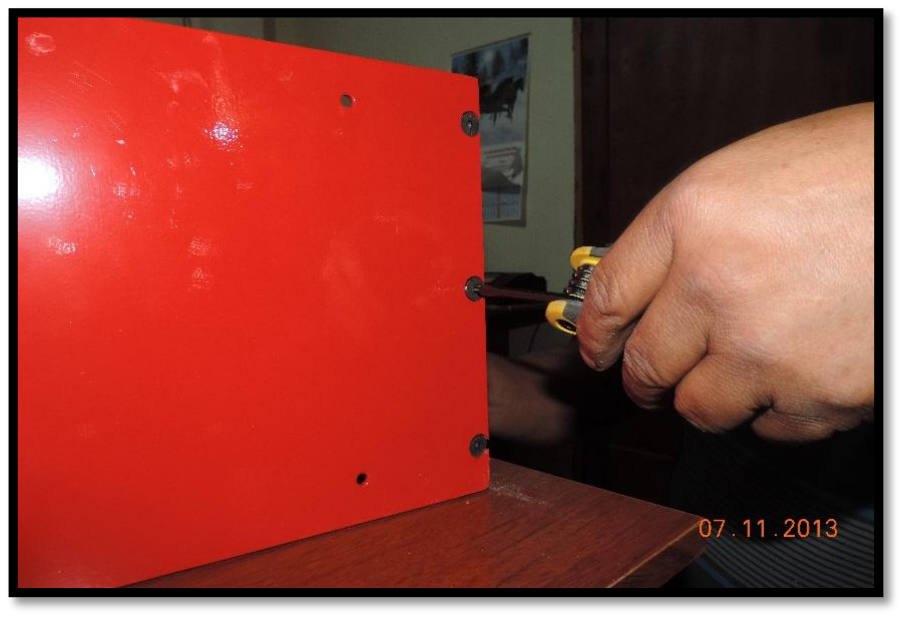
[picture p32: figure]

Fuente: Autor

La sujeción se la realiza con tornillos avellanados de ¾’’. Primero se debe

sujetar la placa del deslizador al tornillo, luego se ajustan las guías y el tornillo

central.

Ilustración 4. Sujeción de la placa del deslizador.

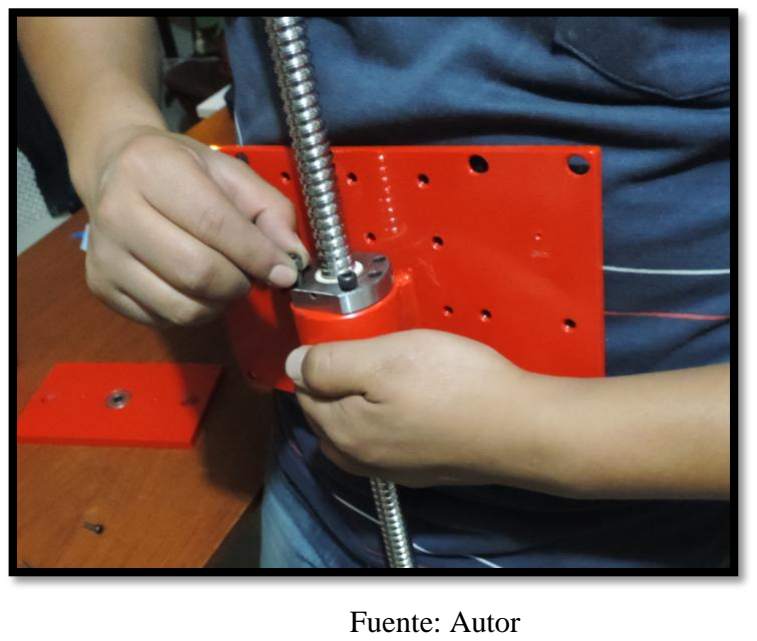
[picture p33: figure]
Fuente: Autor

Ilustración 5. Inserción de las guías

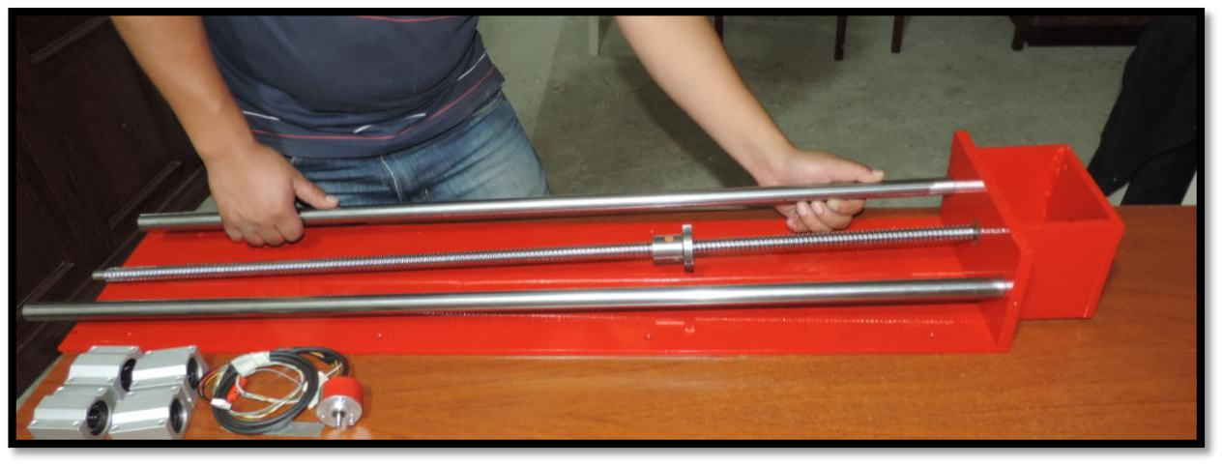
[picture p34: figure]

Seguidamente se colocan los rodamientos lineales en las guías, los mismos

tienen una numeración como se muestra en la imagen para que el ajuste sea el

óptimo.

Fuente: Autor

Ilustración 6. Insertar los rodamientos lineales

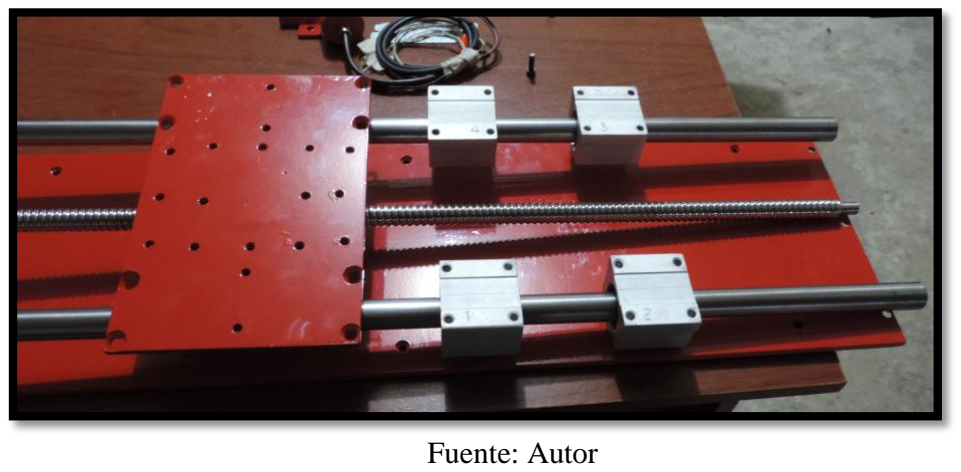
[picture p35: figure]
Fuente: Autor

Ilustración 7. Numeración de los rodamientos.

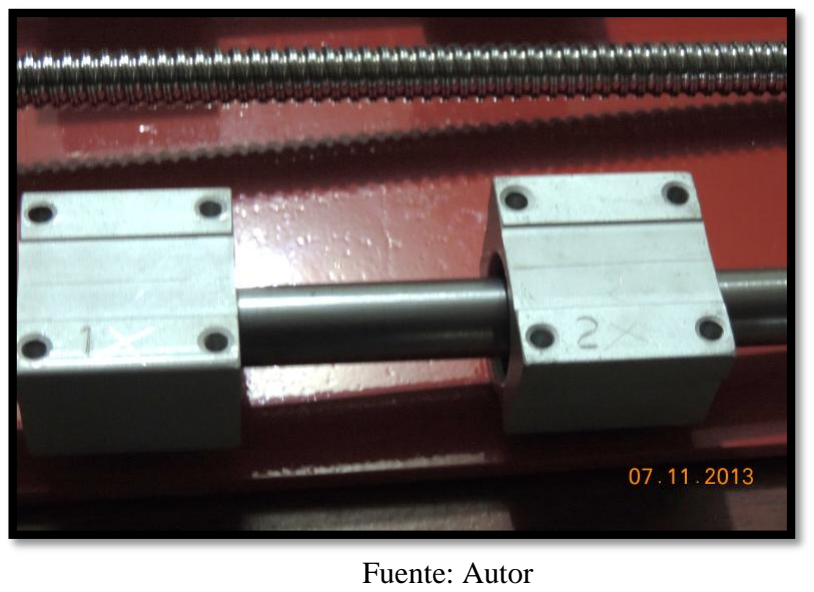
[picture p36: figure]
Fuente: Autor

Para poder asegurar las guías en su lugar se tiene prisioneros de 1/8’’

Ilustración 8.Seguro de la guía

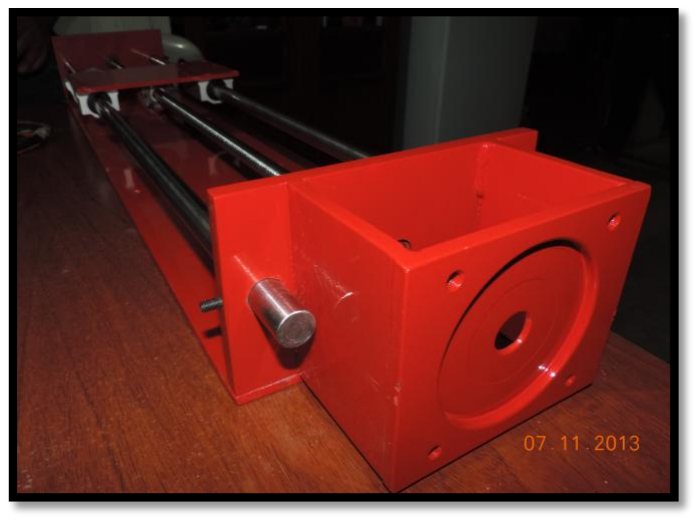
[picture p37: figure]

### 2.2. Tornillo central y base

El tornillo de bolas está compuesto por un tornillo central y su tuerca, ambos

elementos de precisión, entre la tuerca y el tornillo existen pequeñas bolas las

cuales hacen que el movimiento sea suave y preciso.

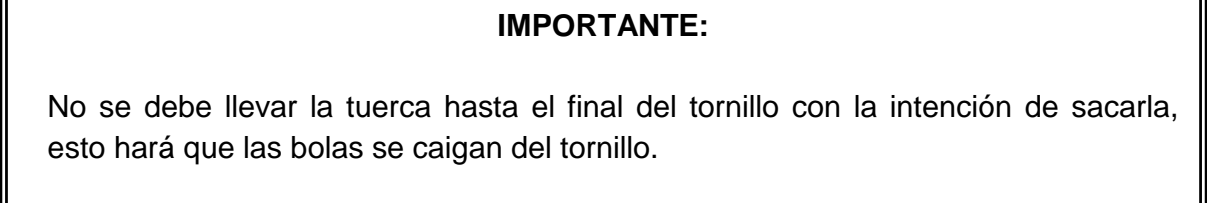
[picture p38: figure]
IMPORTANTE:

Ilustración 9. Tornillo de bolas

No se debe llevar la tuerca hasta el final del tornillo con la intención de sacarla, esto hará que las bolas se caigan del tornillo.

Fuente: Autor

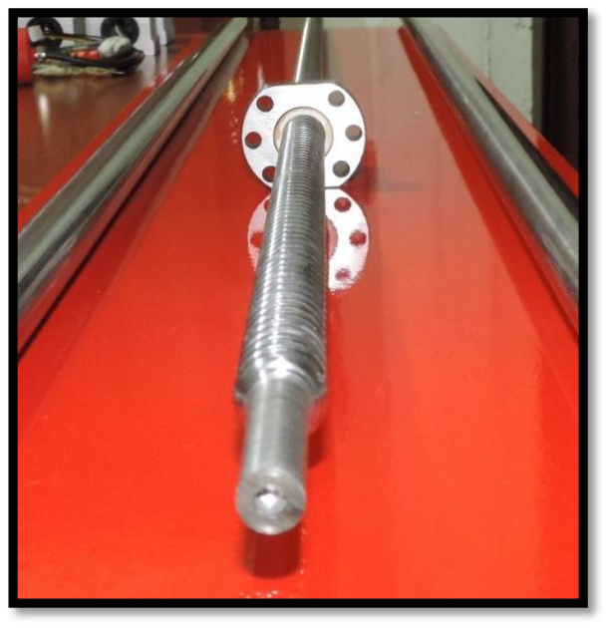
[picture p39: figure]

Fuente: Autor

En uno de sus extremos el tornillo de bolas cuenta con una perforación axial,

esta sirve para que la espiga del encoder sea insertada y de esta forma pueda

girar solidario al tornillo.

### 2.3. Guías y rodamientos

Las guías de los rodamientos son de acero extra duro templado y pulido. La

superficie de la guía se sometió a un proceso de endurecimiento, esto con la

finalidad de prolongar la vida útil de los rodamientos lineales.

Ilustración 10. Tornillos y carro deslizador.

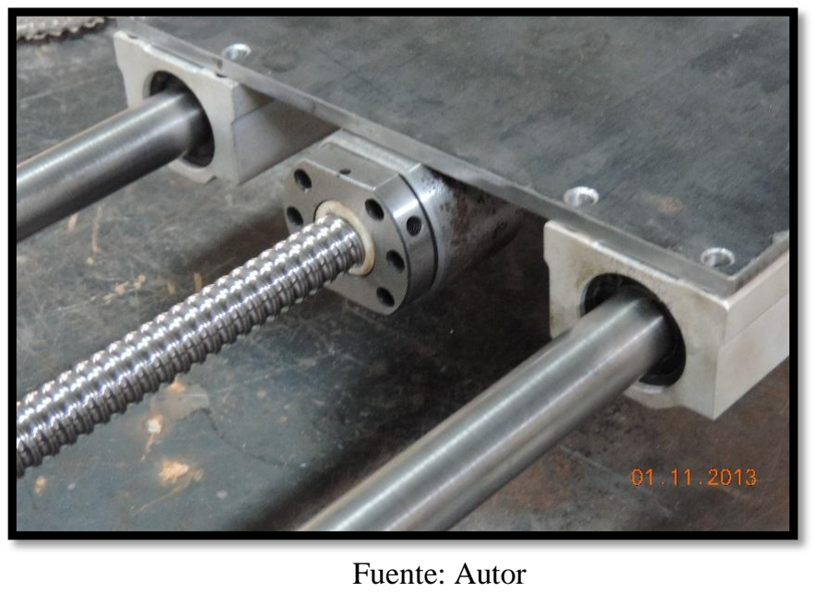
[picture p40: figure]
Fuente: Autor

Es importante mantener la lubricación en las guías como en el tornillo para

prolongar la vida útil de los componentes.

Los rodamientos lineales se componen de los rodamientos LBBR20 SKF, los

cuales internamente también cuentan con bolas re circulantes para disminuir la

fricción de los mismos.

Ilustración 11. Rodamientos SKF LBBR 20

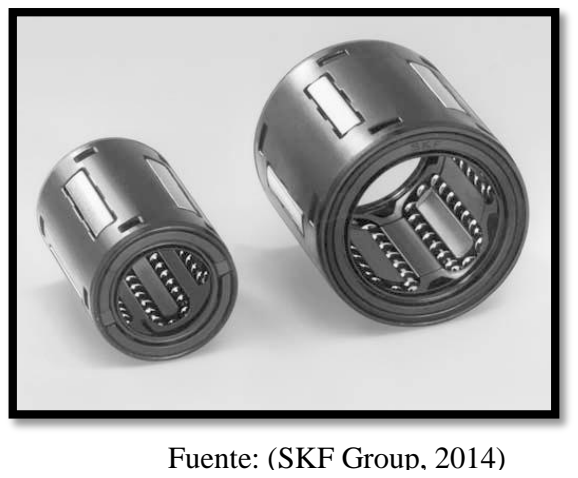
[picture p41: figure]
Fuente: (SKF Group, 2014)

Estos rodamientos se encuentran dentro de sus carcasas de aluminio, las

cuales facilitan la sujeción de la placa del deslizador, estas se realizan mediante

tornillos avellanados de 1/8’’

Ilustración 12. Rodamientos en sus carcasas.

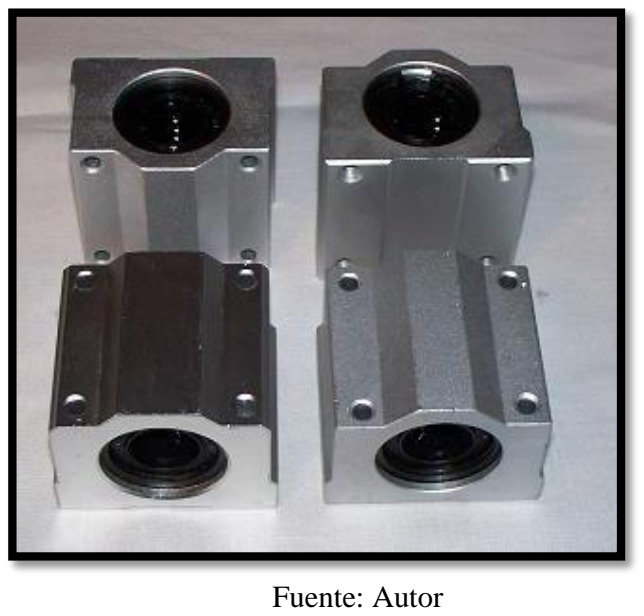
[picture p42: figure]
Fuente: Autor

En caso de ser necesario se puede cambiar el rodamiento manteniendo la

misma carcasa.

### 2.4. Encoder

El módulo cuenta con un encoder de cuadratura Hohner, el cual es conecta al

extremo del tornillo de bolas mediante su sujeción a una placa acopladora que le

permite ser sujeta a la placa del deslizador.

Ilustración 13. Sujeción del encoder.

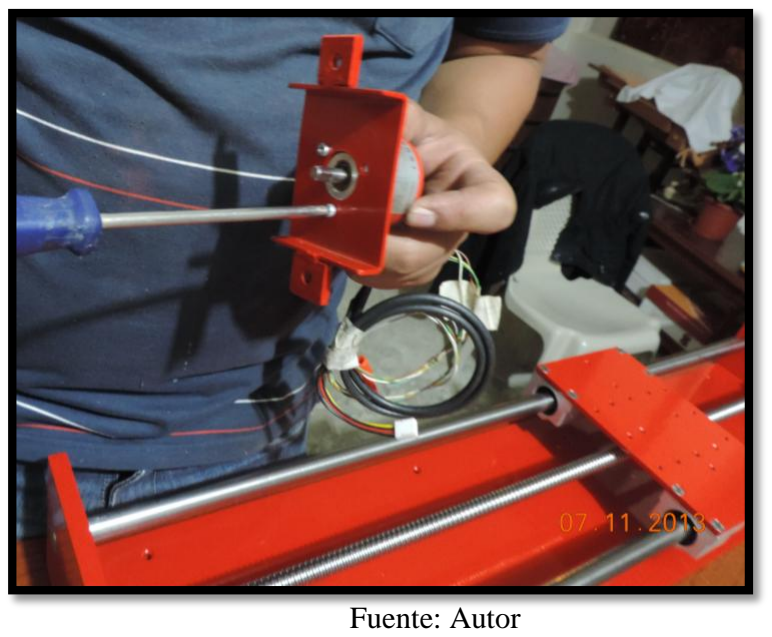
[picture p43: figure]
Fuente: Autor

Los terminales del encoder se encuentran conectados a placa electrónica que

cuenta con la leyenda “CONECTOR ENCODER”. Sus terminales de alimentación

como sus salidas digitales se encuentran debidamente etiquetadas en la placa

electrónica.

Ilustración 14. Acople del encoder al tornillo.

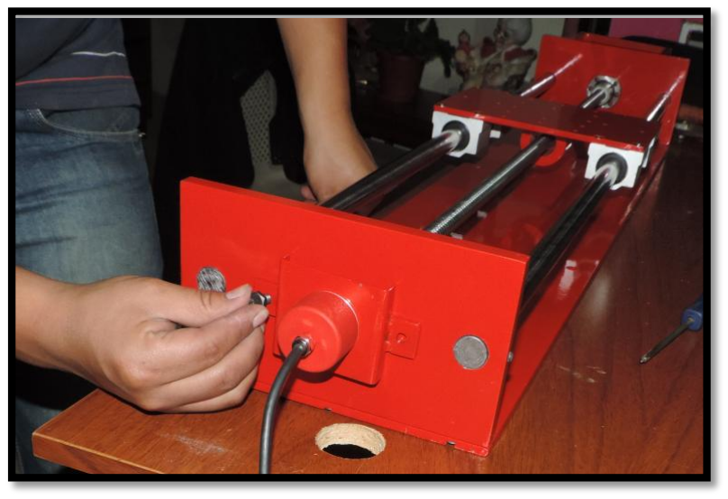
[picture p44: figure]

### 2.5. Servomotor

El servomotor se sujeta al deslizador mediante cuatro tornillos de cabeza

hexagonal de 5/16’’ de diámetro.

Fuente: Autor

Ilustración 15. Sujeción del servomotor.

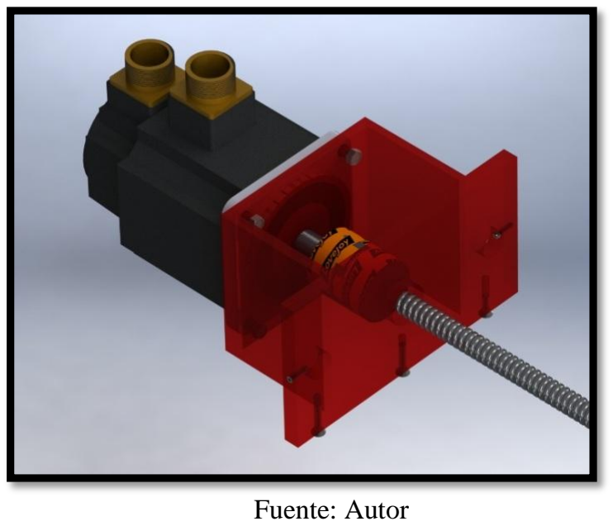
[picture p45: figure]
Fuente: Autor

El servomotor se une al tornillo de bolas mediante el matrimonio Lovejoy. Esta

unión es de vital importancia para el servomotor, ya que de la misma depende la

vibración que se produzca en el deslizador. El ajuste del matrimonio se realiza

mediante prisioneros dentro del mismo acople.

### 3. Electrónica

Para poder realizar el control del servomotor se han diseñado tres placas

electrónicas las cuales se encuentran ubicadas dentro de una caja para mayor

protección.

Dentro de esta caja se encuentran realizadas las conexiones necesarias para

que el módulo funcione de manera adecuada. Los elementos con los que cuenta

son:

Fuente de voltaje de 12Vdc – 3A

Transformador 120Vac-12Vac de 3A

Botón de paro de emergencia

Switch de encendido

Luz piloto, indica el estado de la alimentación 110 Vac

Conector para el servodrive.

Cable de alimentación 24Vdc.

Cable de comunicación serial RS-232.

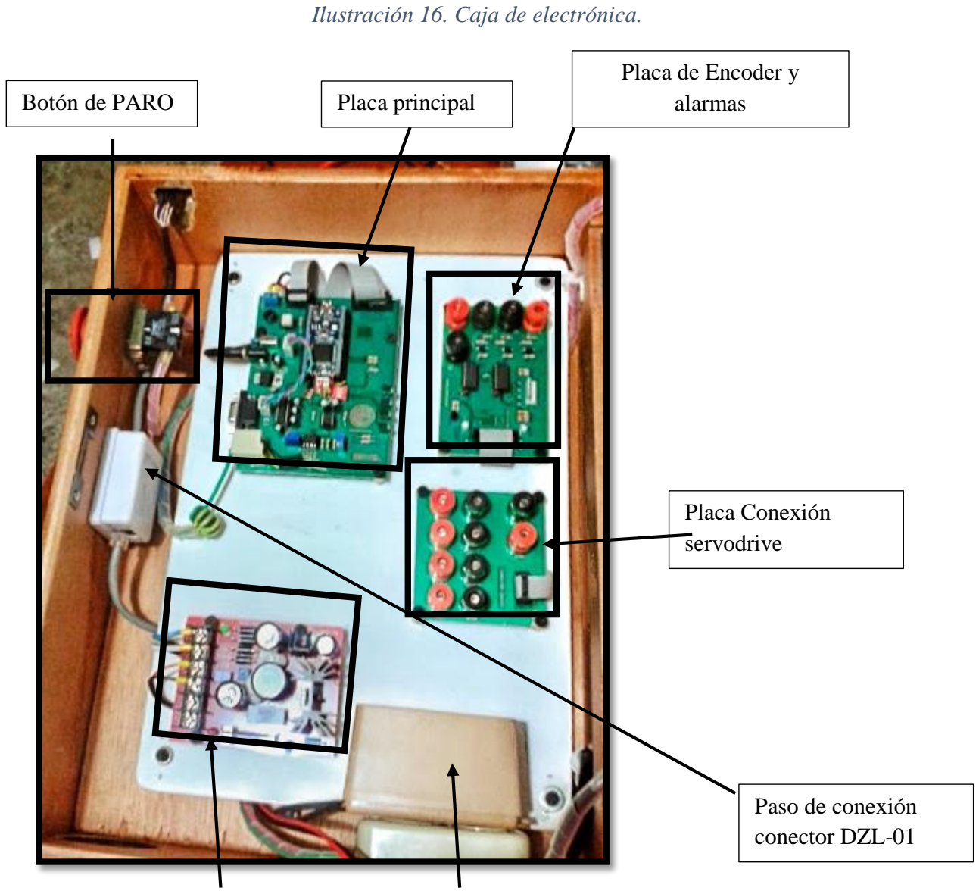
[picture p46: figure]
Ilustración 16. Caja de electrónica.; Placa principal; Placa de Encoder y alarmas; Placa Conexión servodrive; Paso de conexión conector DZL-01; Botón de PARO

### 3.1. Placa de Conexión Servodrive

La placa de borneras tiene la finalidad de conectarse con el servodrive, esa

diseñada para realizar esa conexión mediante conectores de banana, sin

embargo, para mayor facilidad para el estudiante se ha incorporado un conector

DB-15, el cual cuenta con un cable de conexión hacia el servodrive, para facilitar

la instalación de la caja se ha instalado un paso de conexión al cual se conecta un

cable de par trenzado UTP mediante un conector RJ-45, una examinación

minuciosa del cableado facilitará conocer su funcionalidad.

Fuente 12Vdc | Transformador 120Vac – 12 Vac

Ilustración 17. Conector y botón de paro.

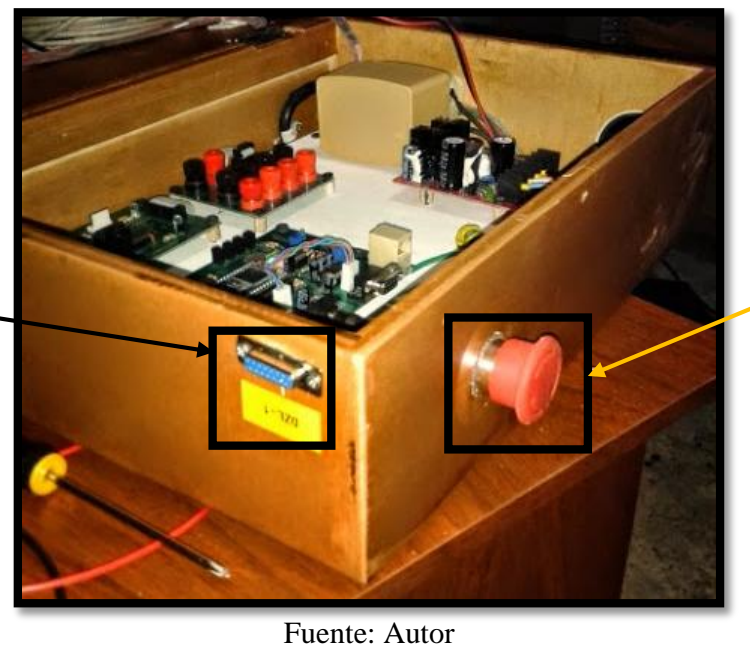
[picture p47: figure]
Fuente: Autor

El cable a utilizar para la conexión con el servodrive se encuentra

debidamente etiquetado como DLZ-01.

Ilustración 18. Cable de comunicación DZL-01

Conector
DZL-01

Botón de
emergencia.

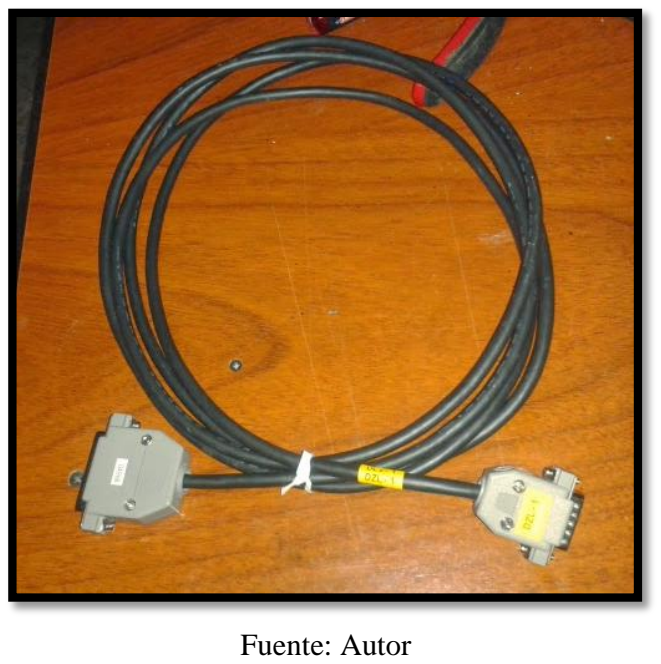
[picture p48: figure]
Fuente: Autor

Ilustración 19. Servodrive GSK DA98D

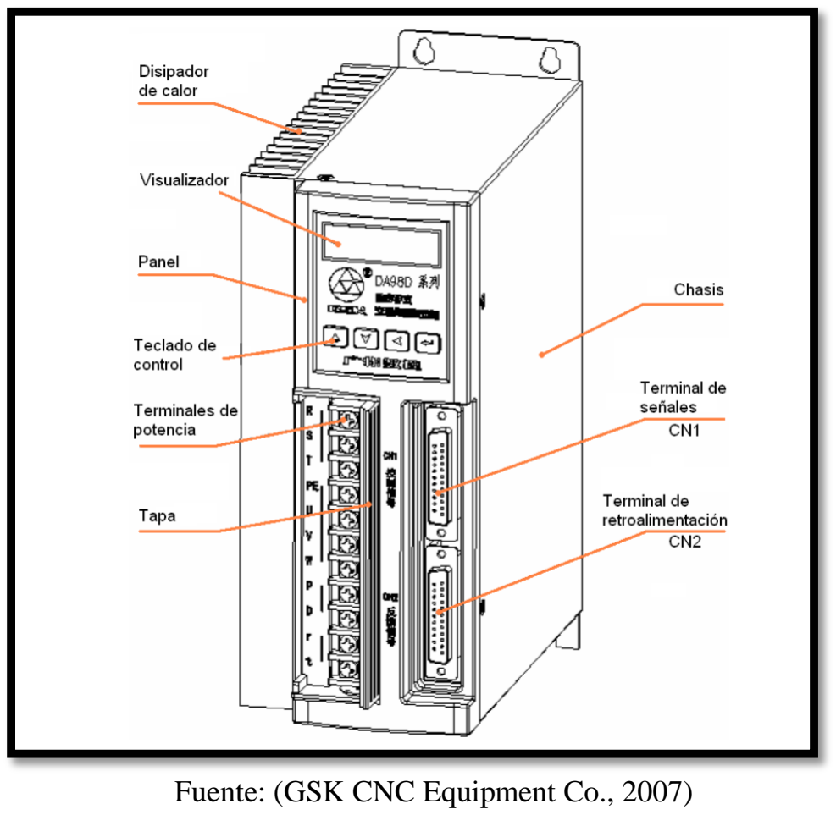
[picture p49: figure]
Fuente: (GSK CNC Equipment Co., 2007)

El cable de conectarse en el terminal CN1 del servodrive.

### 3.2. Placa de encoder y alarmas

La placa de encoder y alarmas está destinada a la adecuación de las señales

provenientes tanto del encoder de cuadratura como de los opto-acopladores

instalados para proveer señales de posición inválidas por parte del carro

deslizador.

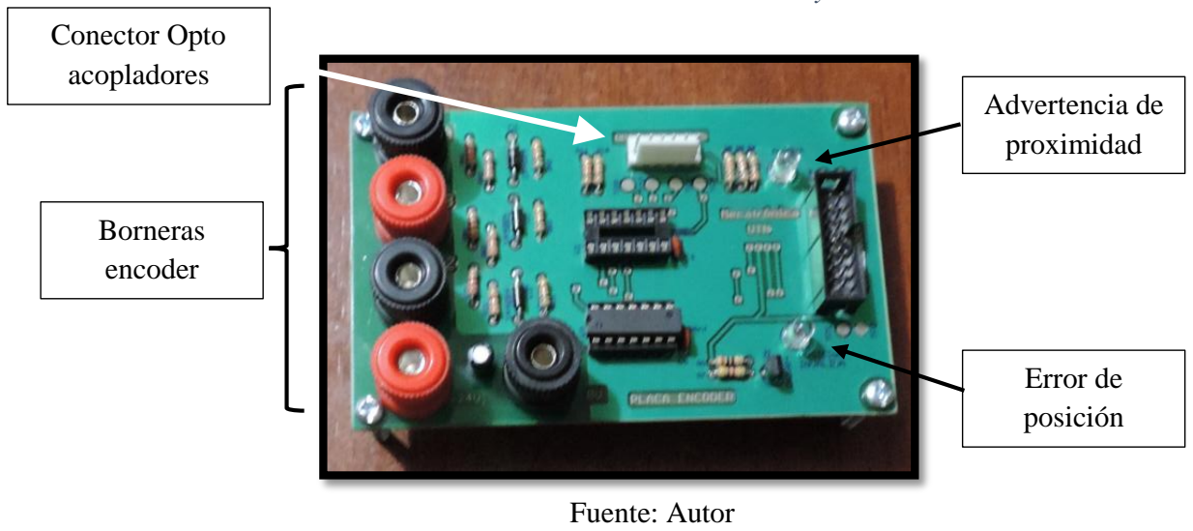
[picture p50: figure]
Advertencia de proximidad; Error de posición; Borneras encoder; Conector Opto acopladores; Fuente: Autor

Ilustración 20. Placa de encoder y alarmas.

El encoder cuenta con las siguientes conexiones.

Tabla 1. Conector de Encoder

Etiqueta | Función
A | Señal de cuadratura A
B | Señal de cuadratura B
Z | Señal de cruce por cero, un pulso por revolución
+ | Alimentación positiva +24VDC
- | Alimentación negativa 0VDC

El conector para opto acopladores es un conector mólex de ocho pines, los

opto acopladores ya se encuentran instalados en el deslizador.

### 3.3. Placa microcontrolador

La placa principal cuenta con el microcontrolador para establecer

comunicaciones con el computador, además en esta placa se encuentran las

conexiones de voltaje que luego son repartidas a las demás placas.

La ilustración 21 se ha agregado a la caja del deslizador para una mejor y

rápida visualización.

Se elaboró un cable RS-232 el cual permitirá conectase con el

microcontrolador a través de su conector DB-9. En este se encuentran

conectados los terminales 2,3 y 5, los cuales corresponden a RX, TX y Tierra para

la comunicación serial.

En caso de ser necesario se puede construir un cable similar de mayor

longitud, se debe tomar en cuenta la velocidad de comunicación serial, ya que es

posible que una longitud elevada pueda deteriorar la transmisión de datos.

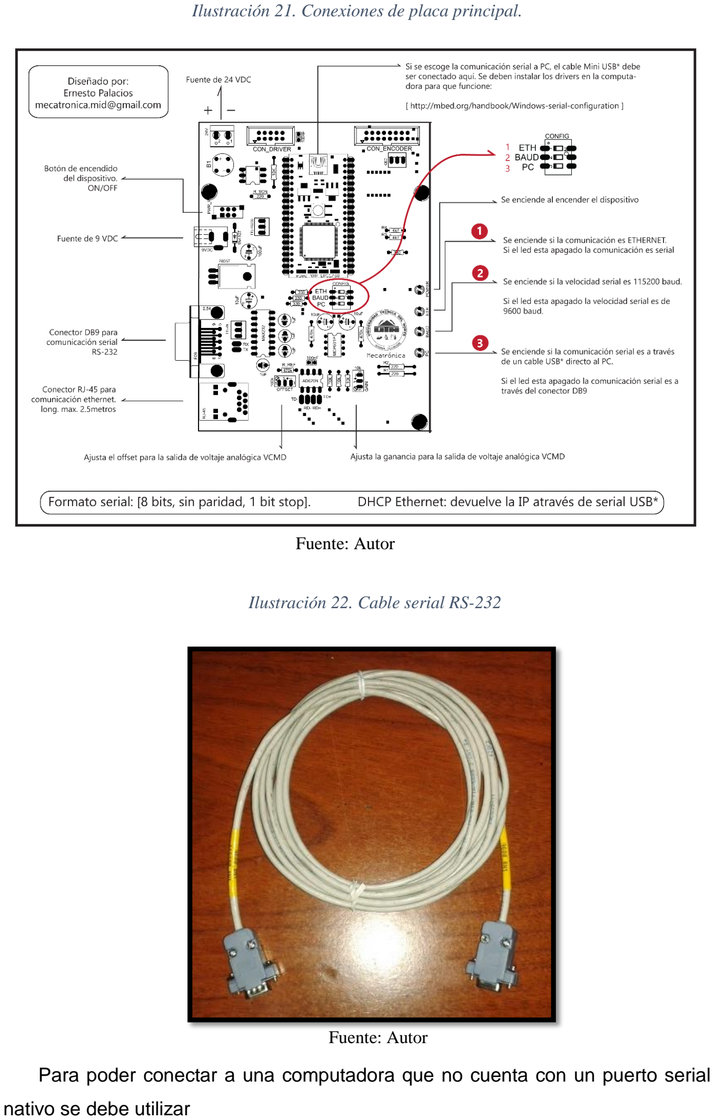
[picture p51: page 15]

Ilustración 21. Conexiones de placa principal.

Ilustración 22. Cable serial RS-232

Para poder conectar a una computadora que no cuenta con un puerto serial

nativo se debe utilizar

Fuente: Autor

Fuente: Autor

Ilustración 23. Cable USB - Serial. TRENDnet TU-S9

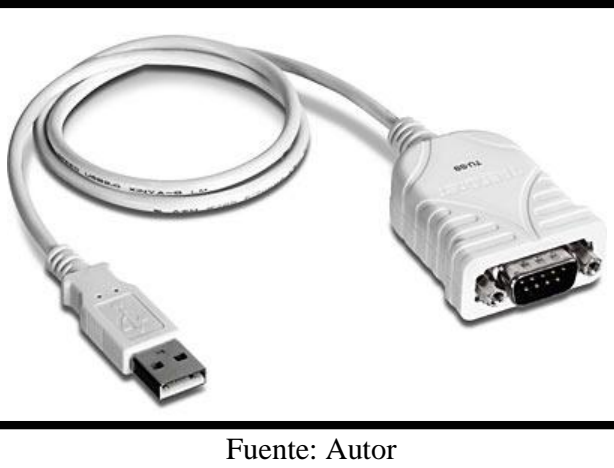
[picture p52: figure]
Fuente: Autor

Para la comunicación ethernet se puede utilizar un cable de red UTP Cat5e,

sin embargo se debe tomar en cuenta que la longitud máxima no debe pasar los

2.5 metros de distancia.

### 4. Mantenimiento

El deslizador cuenta con partes móviles las cuales con el pasar del tiempo

deberán ser reemplazadas, es difícil estimar su tiempo de vida útil ya que no se la

frecuencia con que se utilizará el módulo, sin embargo, en su diseño se ha

sobredimensionado sus elementos de tal manera que puedan durar un gran

periodo de tiempo. El tiempo calculado de vida útil es de 176 (Km) de recorrido.

Los elementos que se deben verificar con frecuencia son los rodamientos,

tanto los lineales que sostienen el deslizador, como los radiales que sostienen el

tornillo. Estos elementos son los que tendrán un mayor desgaste y por lo tanto

serán los primeros en ser reemplazados.

En el caso de ser necesario el reemplazo de algún elemento por favor

referirse a la sección 3.1.3 DESLIZADOR. En esta se detallan la marca y modelo

de los elementos del deslizador.

La velocidad máxima recomendada es de 1500 (RPM), el mantener una

velocidad mayor puede causar daños a los rodamientos y el tornillo debido a la

vibración.

### 4.1. Aplicación de grasa

El mantenimiento del tornillo consiste en la aplicación periódica de grasa

blanca 10-42 3M, este tipo de grasa ayudara a alargar el tiempo de vida del

tornillo. Debido a que es difícil conseguir este tipo de grasa en el mercado local se

sugiere el uso de “grasa azul” la cual es multipropósito y puede ser conseguida

con facilidad.

Se debe aplicar la grasa antes de cualquier práctica que se realice con el

deslizador, de esta manera se asegurará su correcto funcionamiento. Se debe

evitar el contacto de las guías y el tornillo con las manos.

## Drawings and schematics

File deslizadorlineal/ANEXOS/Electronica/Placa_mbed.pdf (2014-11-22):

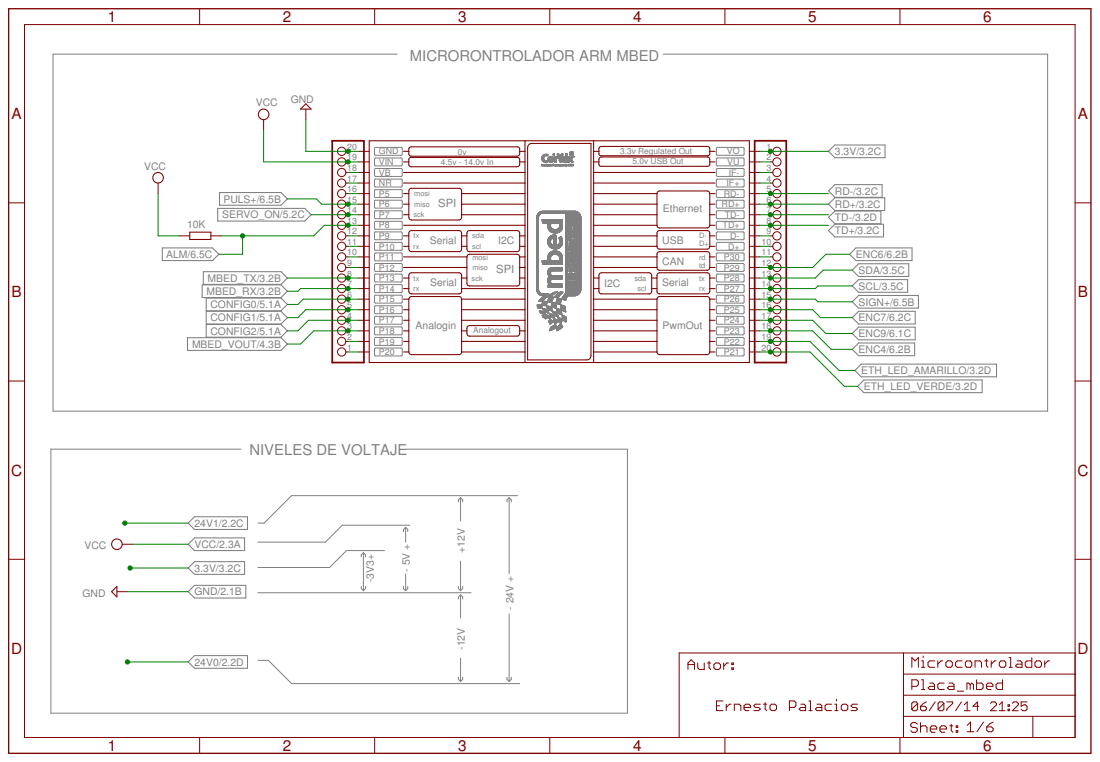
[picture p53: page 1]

3.3v Regulated Out 5.0v USB Out GND

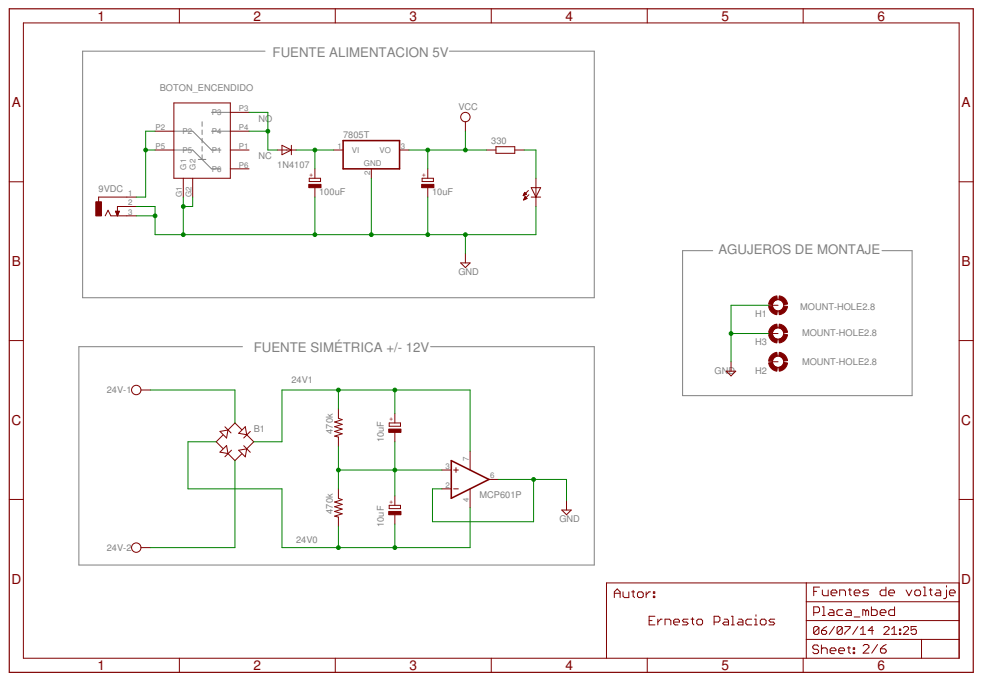
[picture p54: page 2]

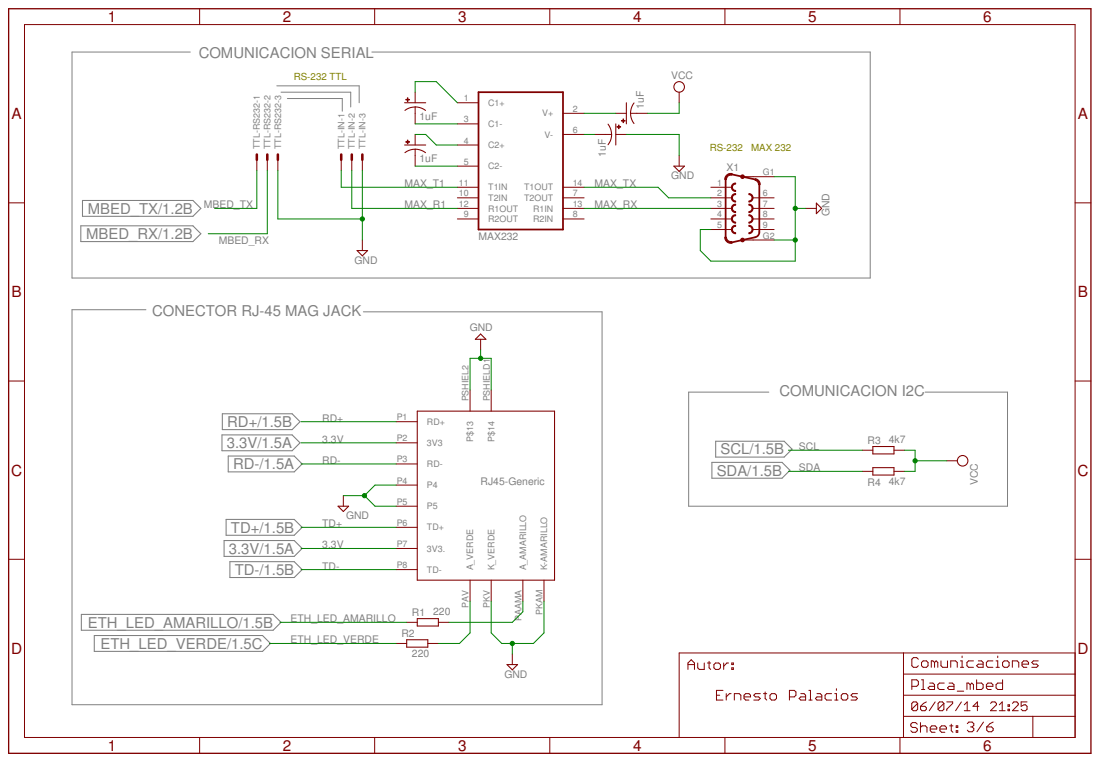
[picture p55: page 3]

TTL-RS232-1 TTL-RS232-2 TTL-RS232-3 TTL-IN-1 TTL-IN-2 TTL-IN-3

CONECTOR RJ-45 MAG JACK

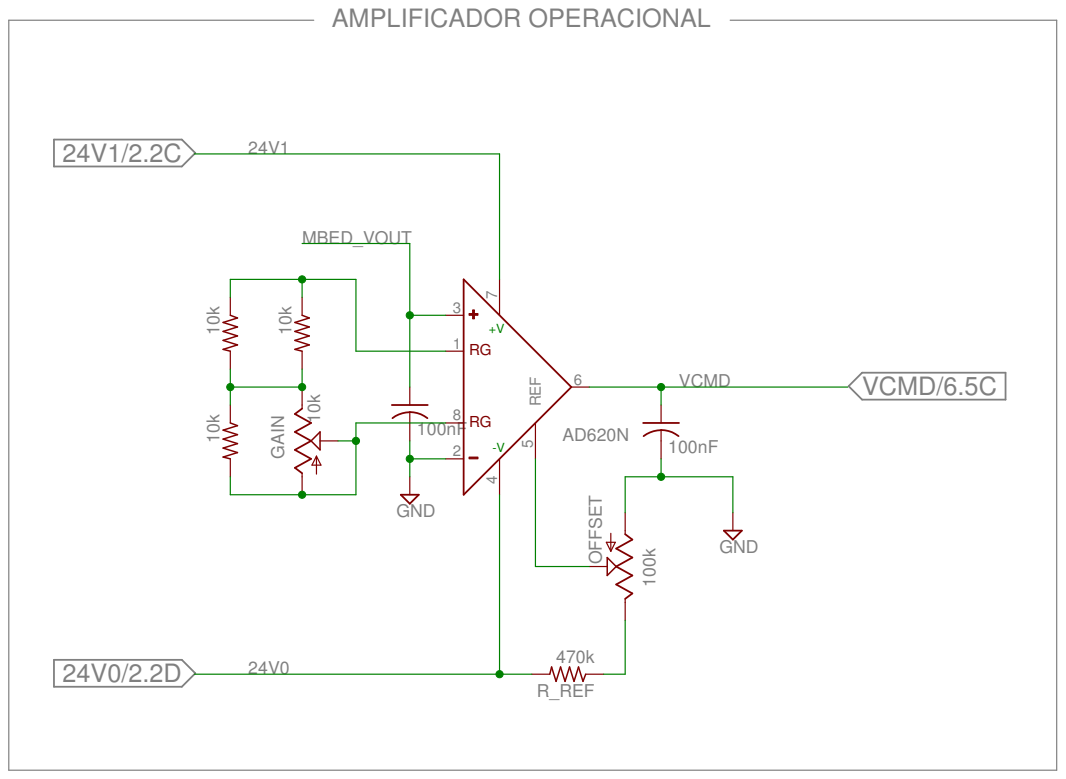
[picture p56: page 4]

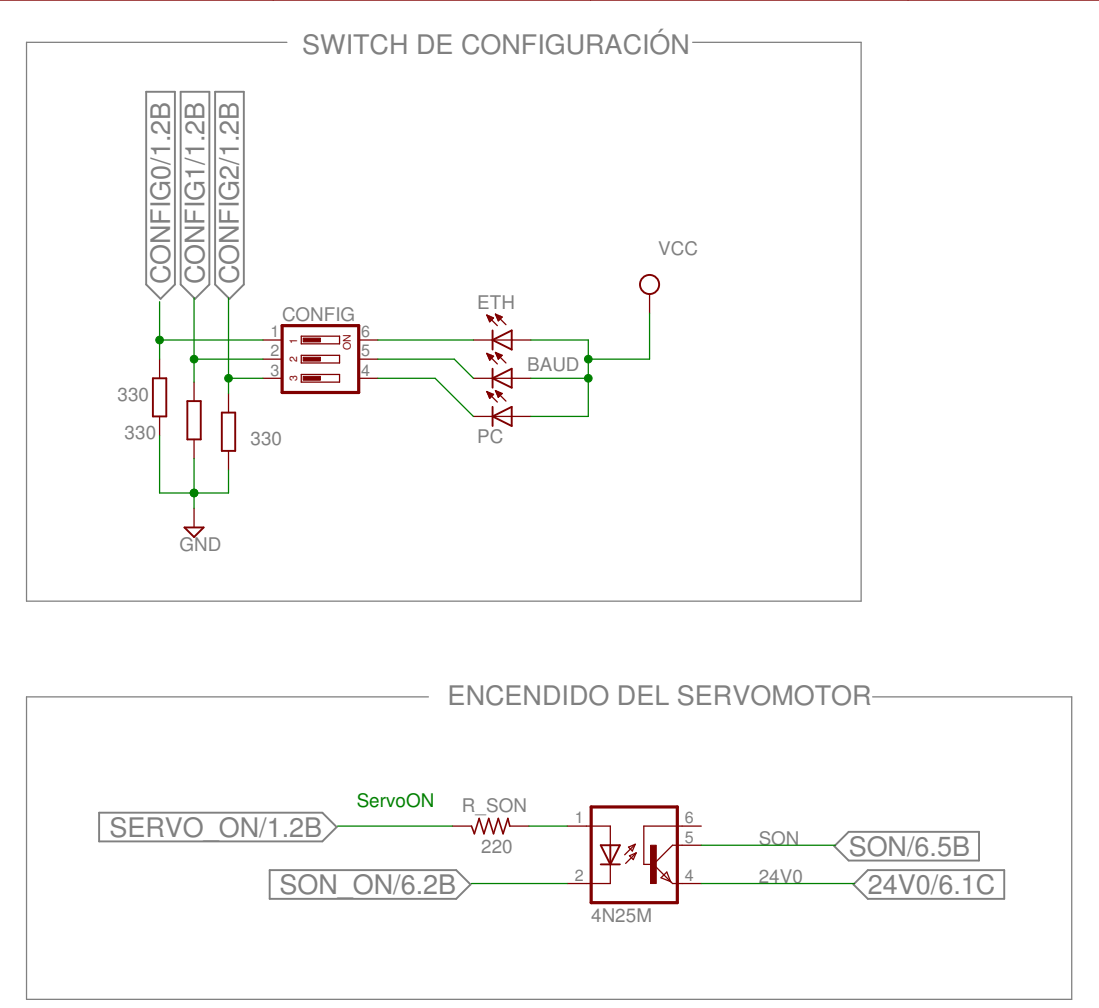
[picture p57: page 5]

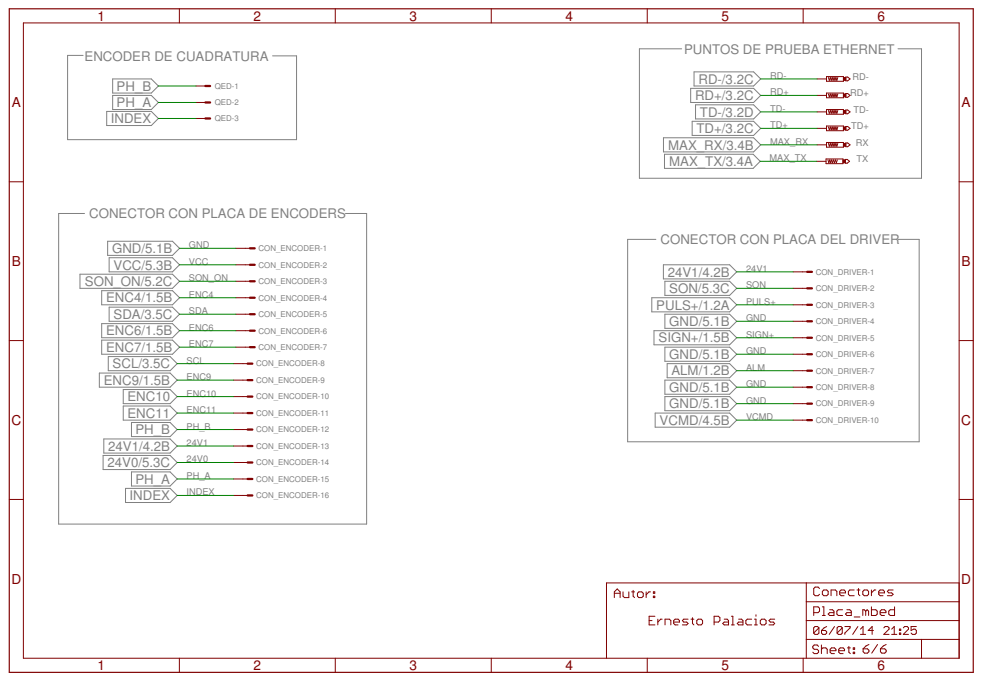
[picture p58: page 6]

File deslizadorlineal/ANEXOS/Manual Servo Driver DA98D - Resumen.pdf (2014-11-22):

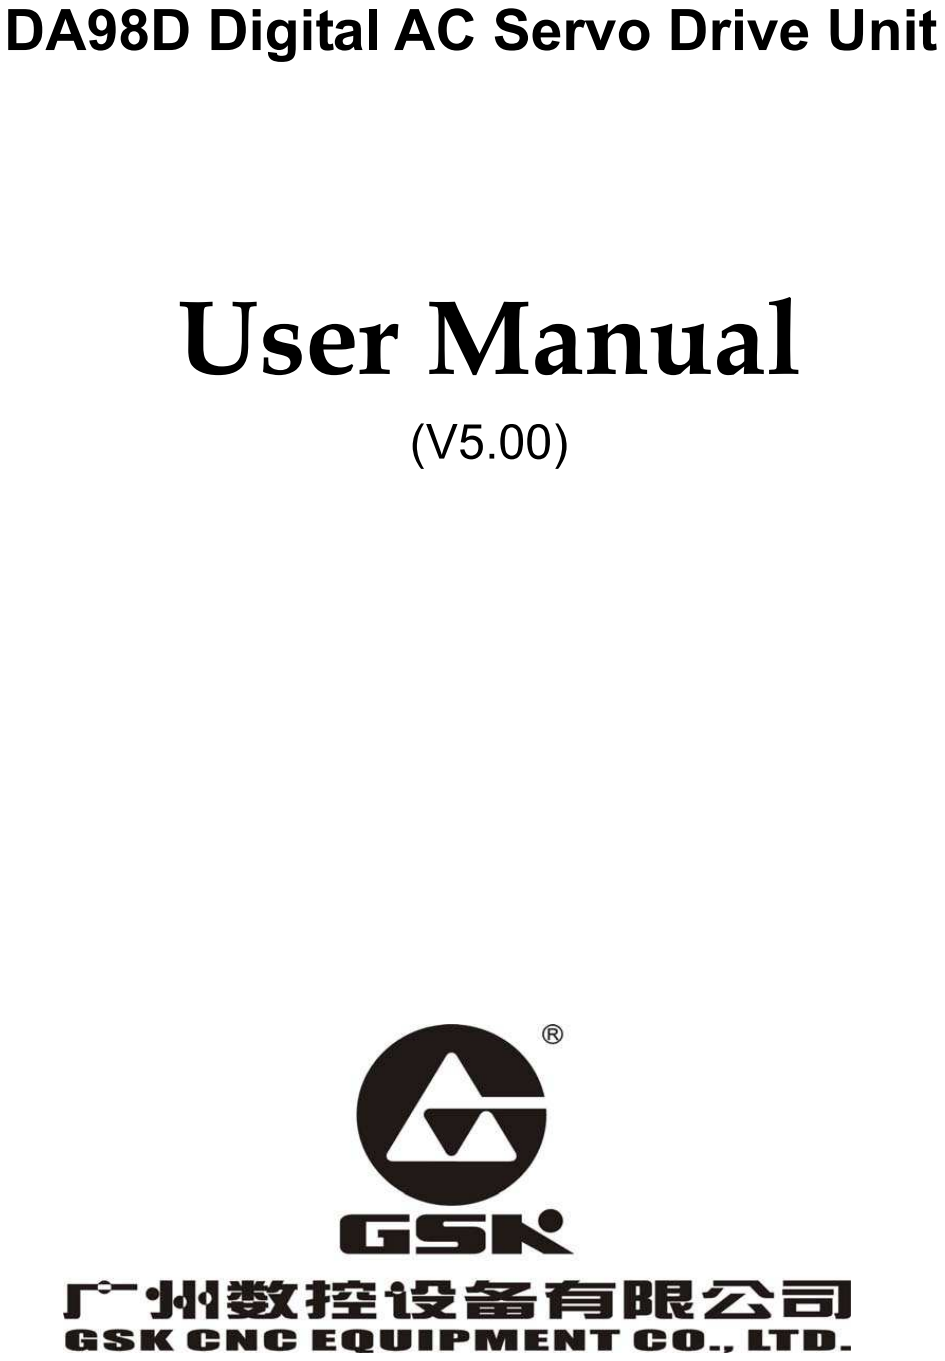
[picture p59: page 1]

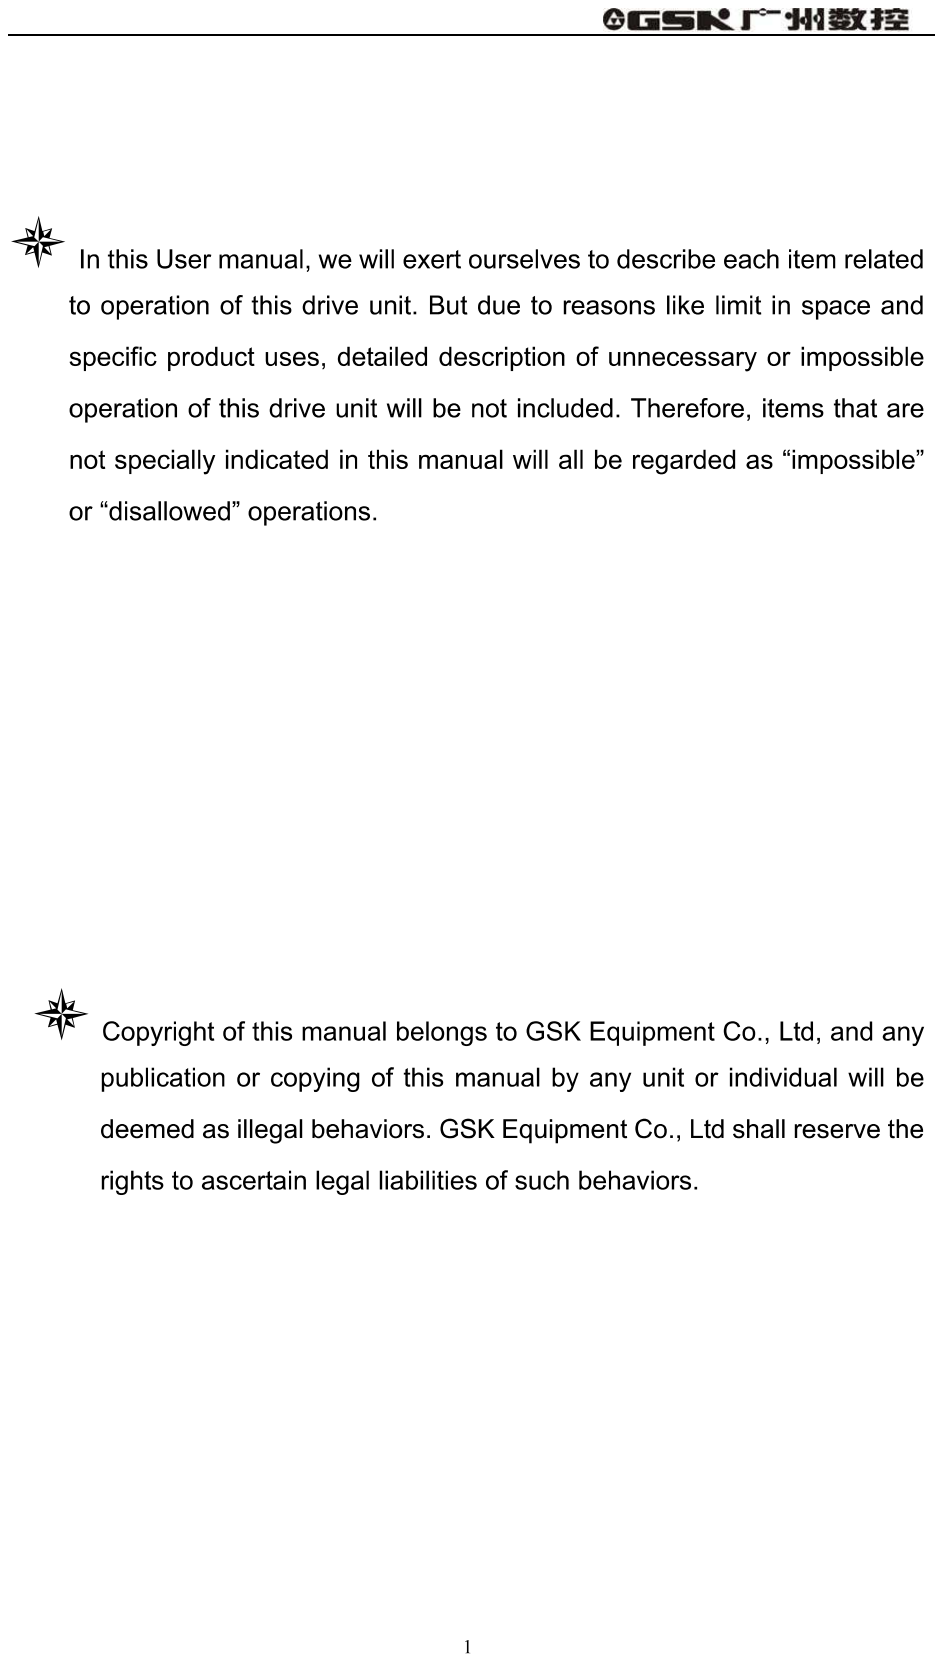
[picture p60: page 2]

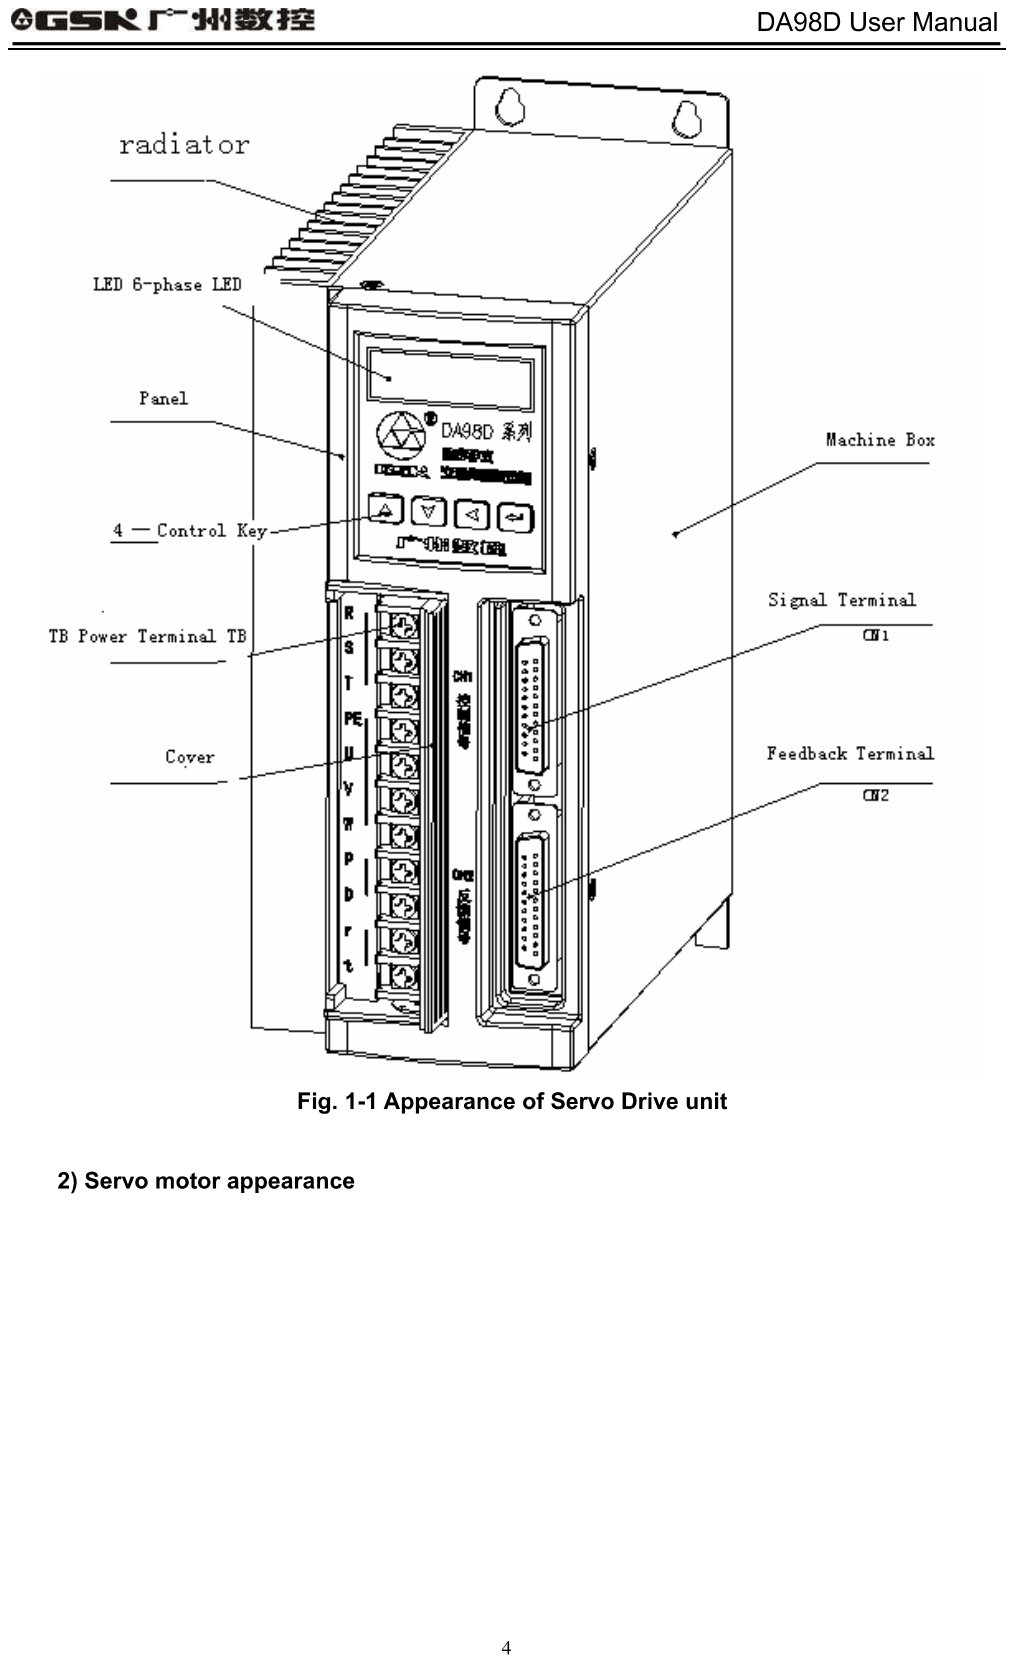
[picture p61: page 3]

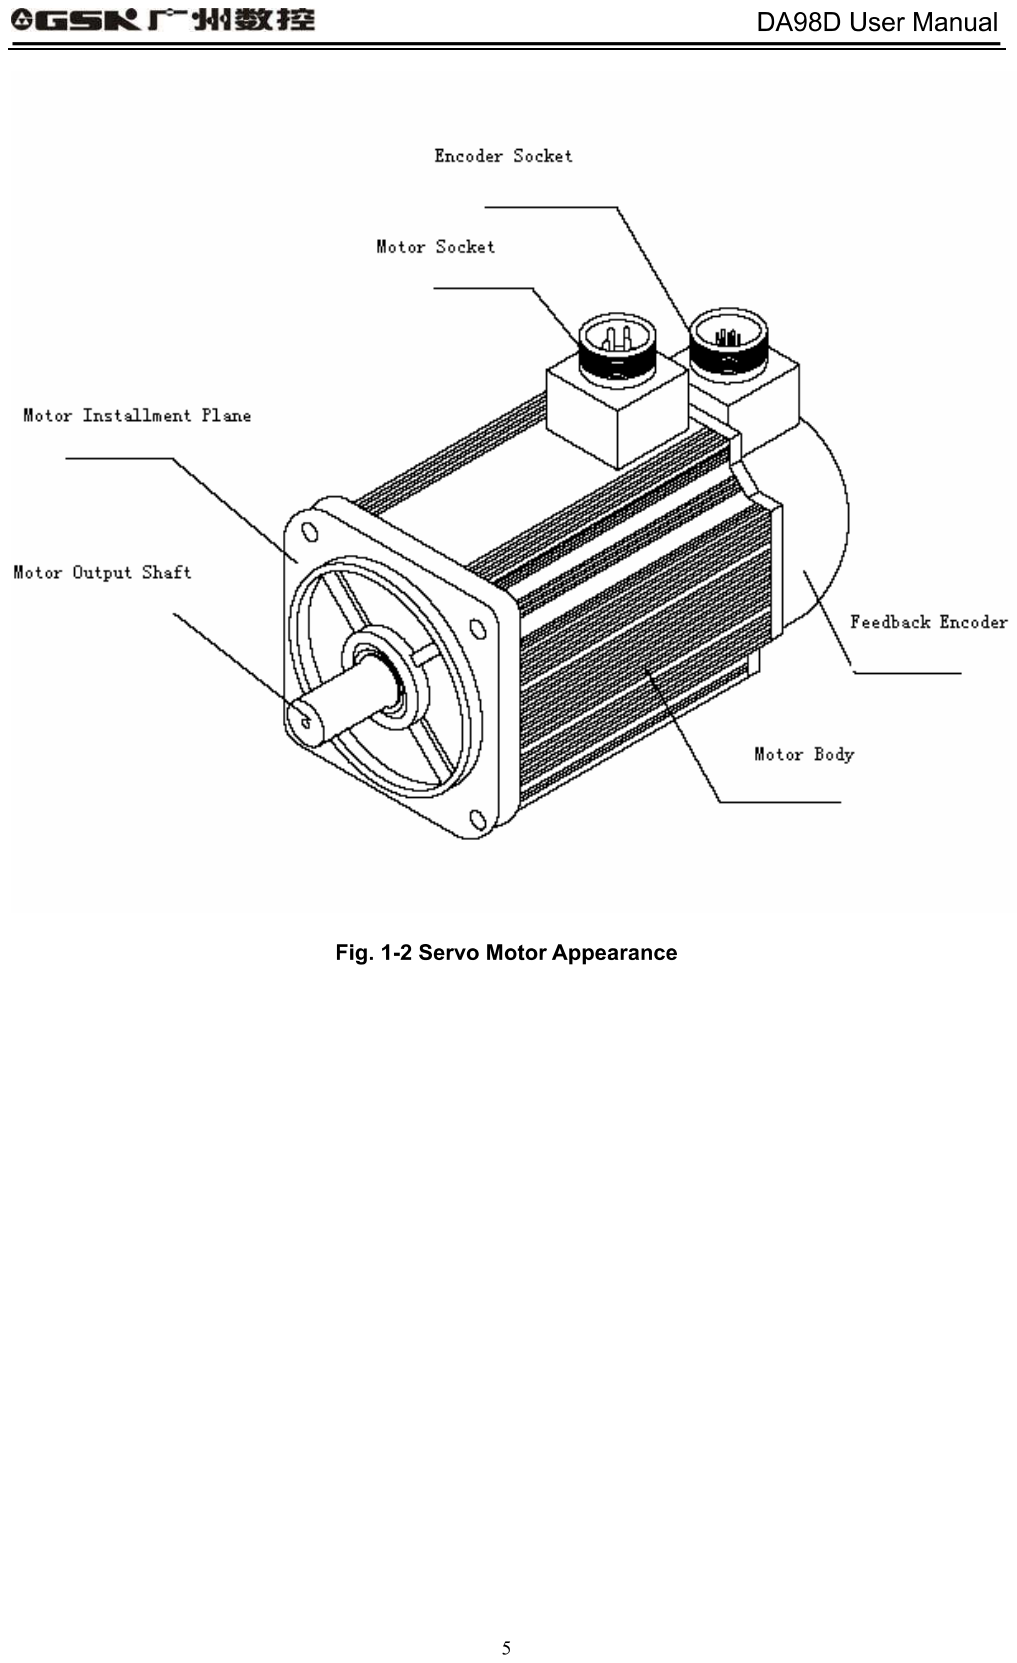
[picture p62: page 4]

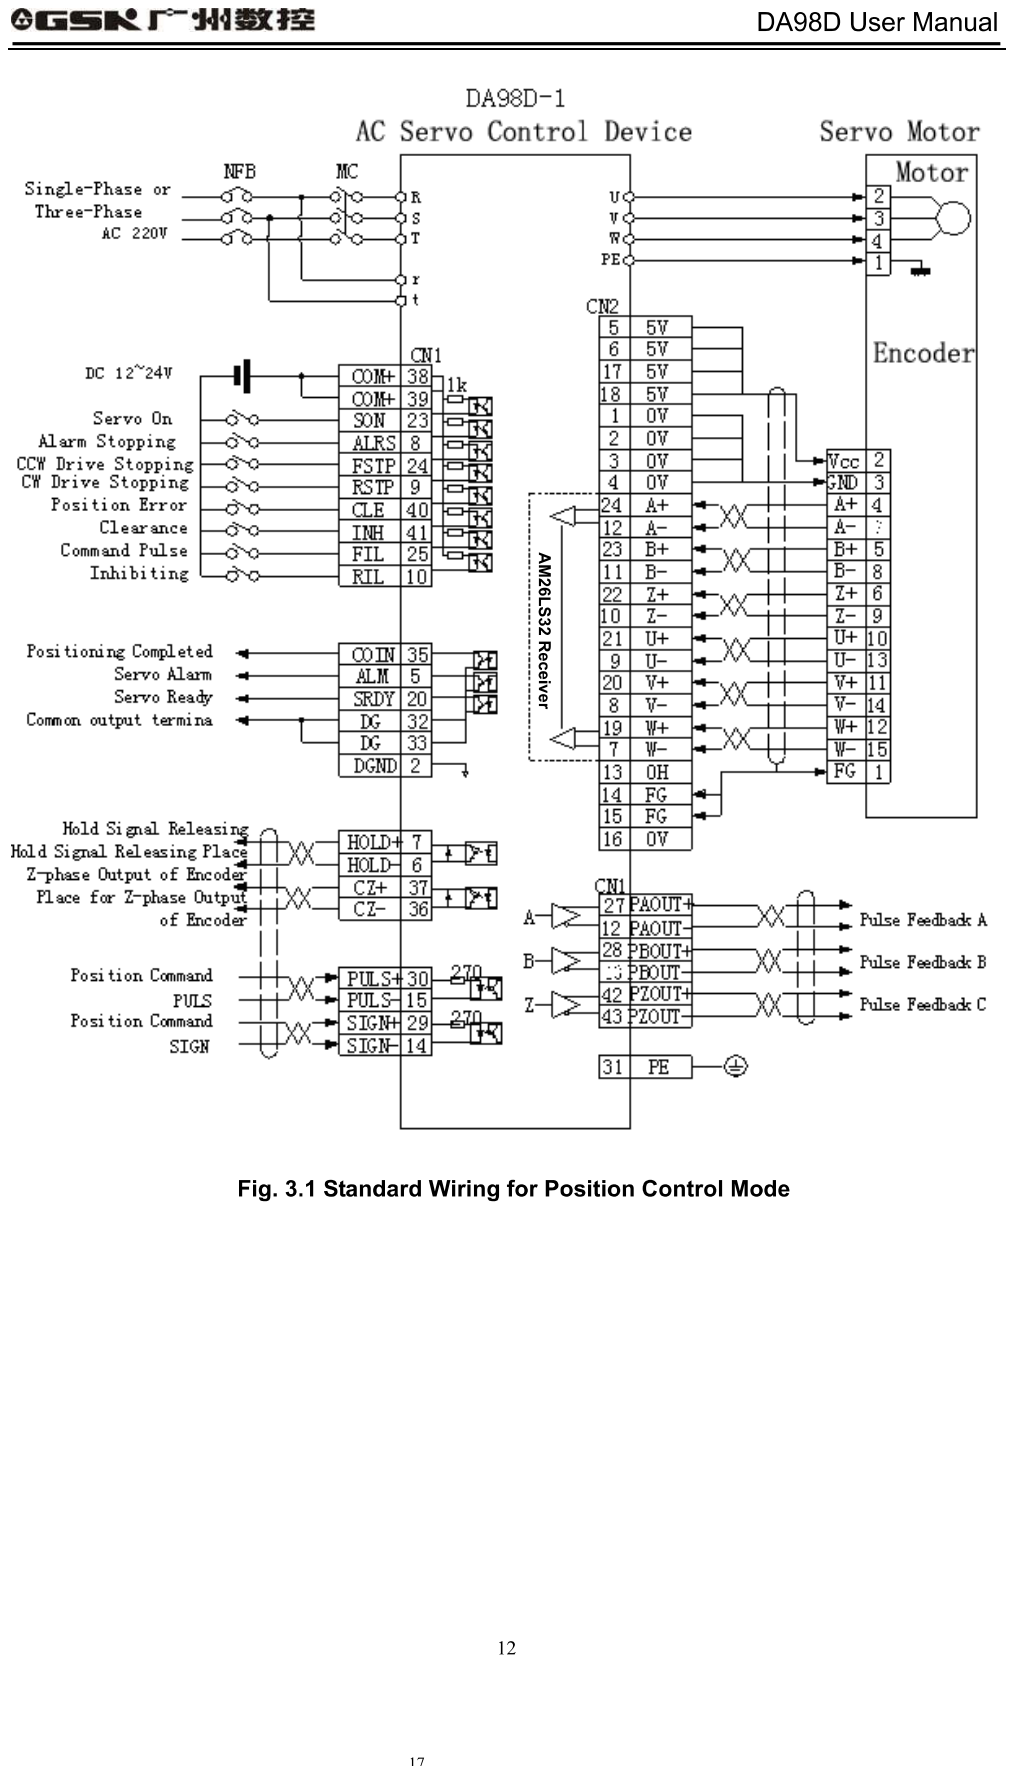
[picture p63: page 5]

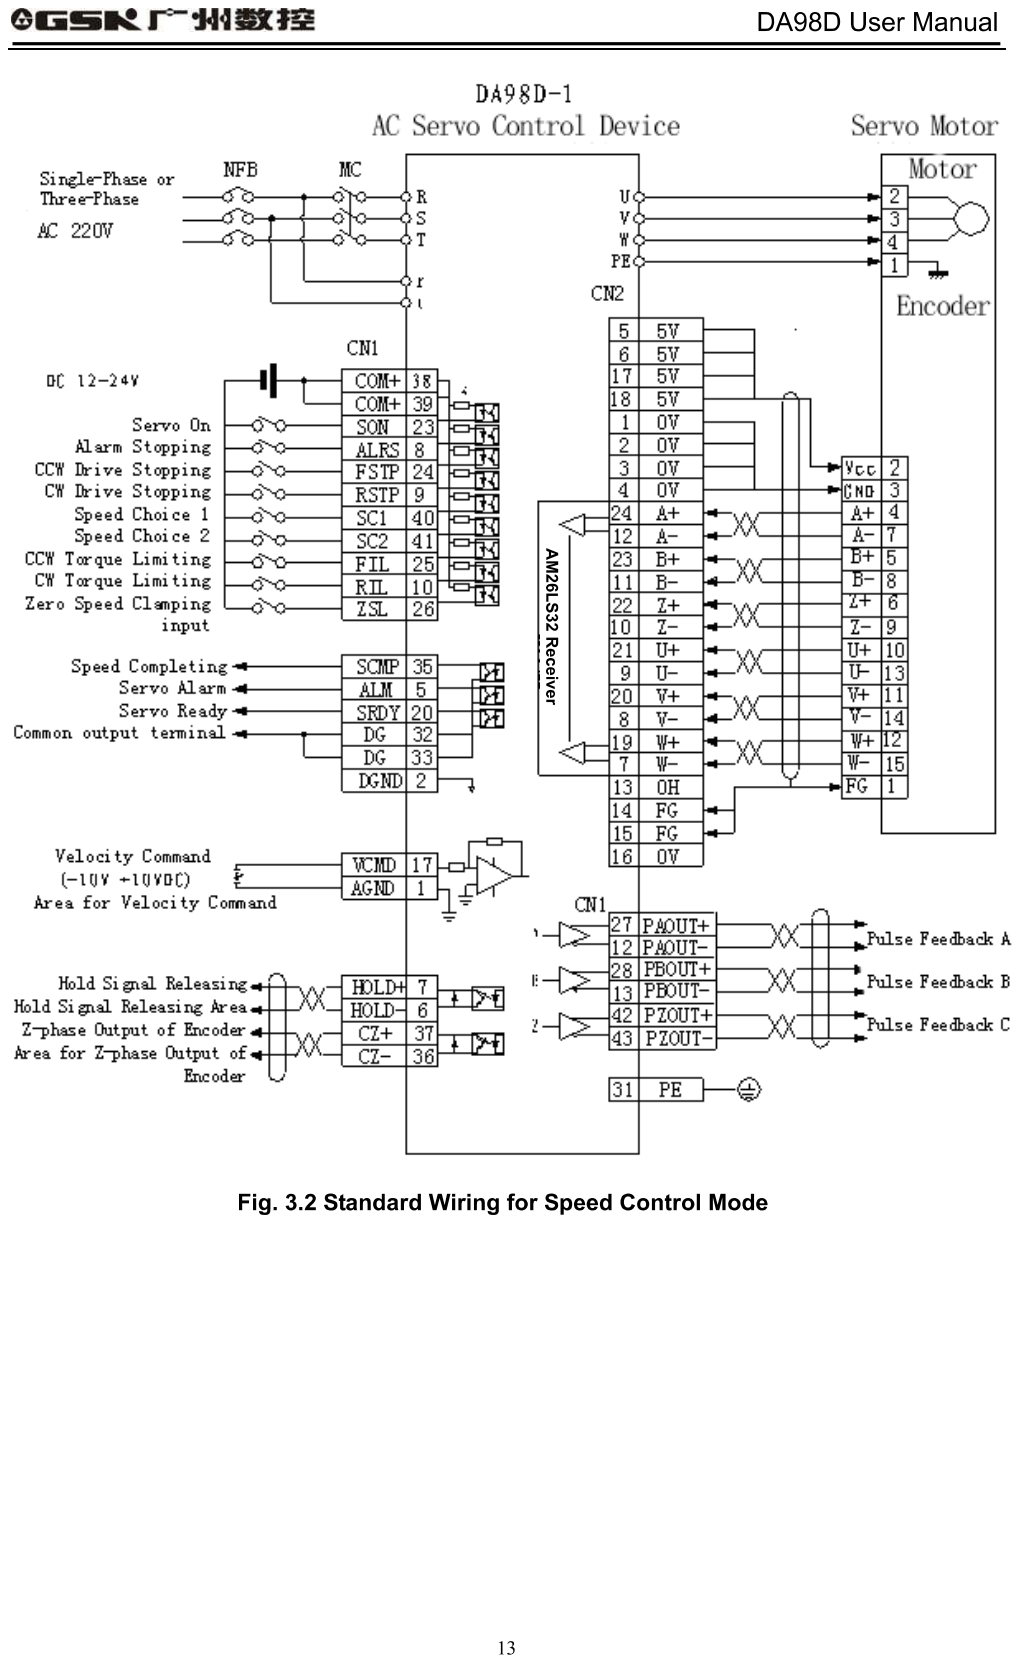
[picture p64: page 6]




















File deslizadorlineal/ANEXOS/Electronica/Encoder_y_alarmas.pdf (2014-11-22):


Salidas de sesores - optoacopladores
VCC

La salida de EMERGENCIA se activan con los opto-acopladores Lim_1 y Lim_4
La salida de ALARMA se activa con los optpacopladores Lim_2 y Lim_3


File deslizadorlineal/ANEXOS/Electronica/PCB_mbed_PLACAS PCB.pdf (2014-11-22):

ETH; BAUD; R_REF; 4N25M R_SON; MCP601P; CONFIG; MAX232; PWR_BTN; CON_DRIVER; CON_ENCODER; TTL-RS232; TTL-IN; OFFSET; QED

POWER ETH BAUD PC


16/07/2014 16:56:44 mirrored D:\Proyecto de Tesis\mbed\Esquema_Circuito\version_final\Placa_mbed.brd


16/07/2014 16:56:07 D:\Proyecto de Tesis\mbed\Esquema_Circuito\version_final\Placa_mbed.brd



16/07/2014 16:59:18 mirrored D:\Proyecto de Tesis\mbed\Esquema_Circuito\version_final\Encoder_y_alarmas_CORREGIDO.brd


16/07/2014 16:59:43 D:\Proyecto de Tesis\mbed\Esquema_Circuito\version_final\Encoder_y_alarmas_CORREGIDO.brd


16/07/2014 17:00:53 mirrored D:\Proyecto de Tesis\mbed\Esquema_Circuito\version_final\conector_driver.brd


16/07/2014 17:01:18 mirrored D:\Proyecto de Tesis\mbed\Esquema_Circuito\version_final\conector_driver.brd


16/07/2014 17:01:56 D:\Proyecto de Tesis\mbed\Esquema_Circuito\version_final\conector_driver.brd

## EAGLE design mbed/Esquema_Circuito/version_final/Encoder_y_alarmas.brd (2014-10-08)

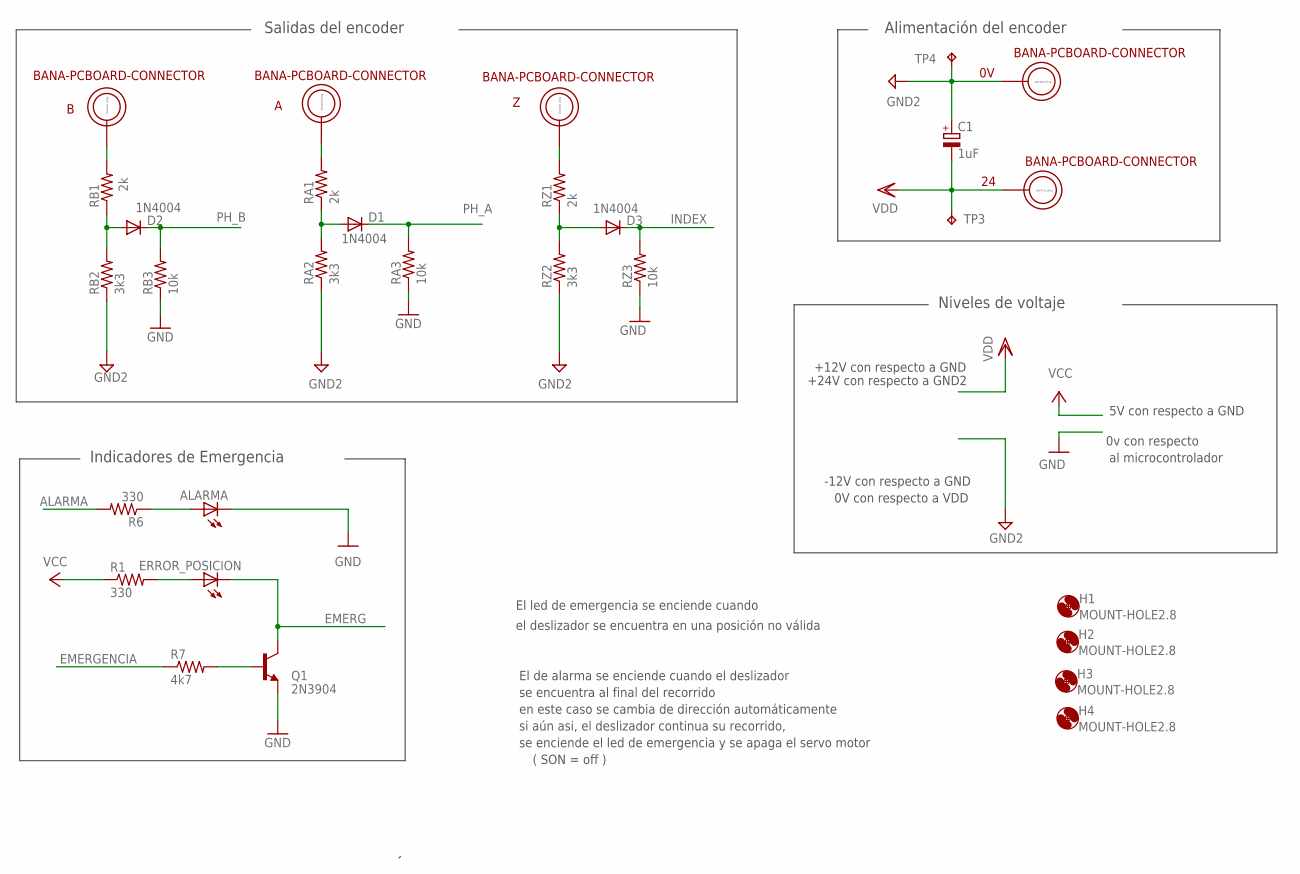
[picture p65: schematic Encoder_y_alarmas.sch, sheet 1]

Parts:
0V, 24: BANA-PCBOARD-CONNECTOR; BANA_PLUG
A: BANA-PCBOARD-CONNECTOR; BANA_PLUG
ALARMA: LED5MM
B: BANA-PCBOARD-CONNECTOR; BANA_PLUG
C1: 1uF; E2,5-6
D1, D2, D3: 1N4004; DO41-10
ERROR_POSICION: LED5MM
H1, H2, H3, H4: MOUNT-HOLE2.8; 2,8
Q1: 2N3904; TO92
R1, R6: 330; 0204/7
R7: 4k7; 0204/7
RA1: 2k; 0204/7
RA2: 3k3; 0204/7
RA3: 10k; 0204/7
RB1: 2k; 0204/7
RB2: 3k3; 0204/7
RB3: 10k; 0204/7
RZ1: 2k; 0204/7
RZ2: 3k3; 0204/7
RZ3: 10k; 0204/7
TP3, TP4: TPB2,54; B2,54
Z: BANA-PCBOARD-CONNECTOR; BANA_PLUG

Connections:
ALARMA: R6.2; also elsewhere on the board
EMERG: ERROR_POSICION.K (C), Q1.1 (C); also elsewhere on the board
EMERGENCIA: R7.1; also elsewhere on the board
GND: ALARMA.K (C), Q1.3 (E), RA3.1, RB3.1, RZ3.1; also elsewhere on the board
GND2: 0V.P$1, C1.+, RA2.1, RB2.1, RZ2.1, TP4.TP; also elsewhere on the board
INDEX: D3.C, RZ3.2; also elsewhere on the board
unnamed: Q1.2 (B), R7.2
unnamed: ERROR_POSICION.A, R1.2
unnamed: ALARMA.A, R6.1
unnamed: D1.A, RA1.1, RA2.2
unnamed: D2.A, RB1.1, RB2.2
unnamed: RZ1.2, Z.P$1
unnamed: B.P$1, RB1.2
unnamed: A.P$1, RA1.2
unnamed: D3.A, RZ1.1, RZ2.2
PH_A: D1.C, RA3.2; also elsewhere on the board
PH_B: D2.C, RB3.2; also elsewhere on the board
VCC: R1.1; also elsewhere on the board
VDD: 24.P$1, C1.-, TP3.TP; also elsewhere on the board

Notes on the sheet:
0v con respecto
5V con respecto a GND
+12V con respecto a GND
+24V con respecto a GND2
-12V con respecto a GND
0V con respecto a VDD
El led de emergencia se enciende cuando
el deslizador se encuentra en una posición no válida
El de alarma se enciende cuando el deslizador
se encuentra al final del recorrido
en este caso se cambia de dirección automáticamente
si aún asi, el deslizador continua su recorrido,
se enciende el led de emergencia y se apaga el servo motor
( SON = off )
Indicadores de Emergencia
Salidas del encoder
Alimentación del encoder
Niveles de voltaje
al microcontrolador

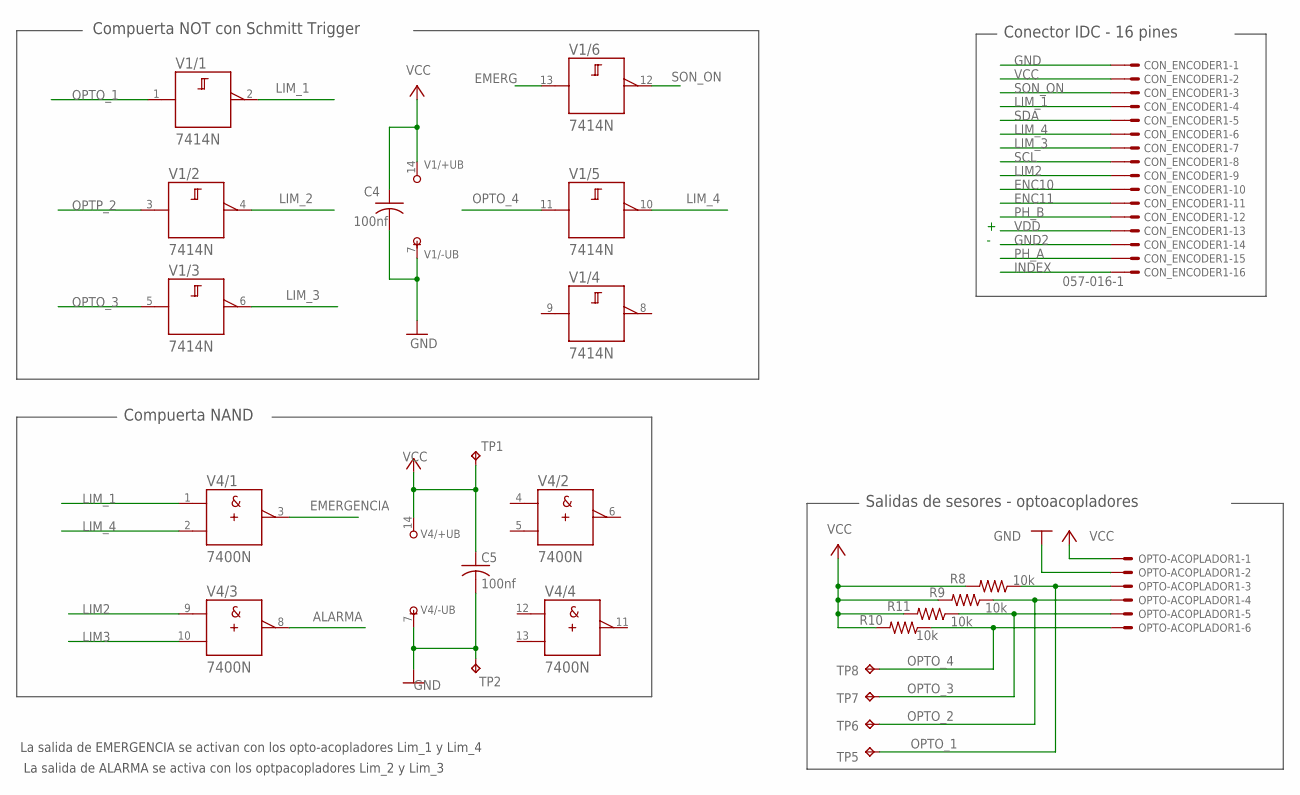
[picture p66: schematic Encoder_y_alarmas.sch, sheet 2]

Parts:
C4, C5: 100nf; C025-024X044
CON_ENCODER1: 057-016-1
OPTO-ACOPLADOR1: 22-23-2061
R8, R9, R10, R11: 10k; 0204/7
TP1, TP2, TP5, TP6, TP7, TP8: TPB2,54; B2,54
V1: 7414N; DIL14
V4: 7400N; DIL14

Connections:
ALARMA: V4.8 (Y); also elsewhere on the board
EMERG: V1.13 (A); also elsewhere on the board
EMERGENCIA: V4.3 (Y); also elsewhere on the board
ENC10: CON_ENCODER1.10
ENC11: CON_ENCODER1.11
GND: C4.2, C5.2, CON_ENCODER1.1, OPTO-ACOPLADOR1.2, TP2.TP, V1.7 (-UB), V4.7 (-UB); also elsewhere on the board
GND2: CON_ENCODER1.14; also elsewhere on the board
INDEX: CON_ENCODER1.16; also elsewhere on the board
LIM2: CON_ENCODER1.9, V4.9 (A)
LIM3: V4.10 (B)
LIM_1: CON_ENCODER1.4, V1.2 (Y), V4.1 (A)
LIM_2: V1.4 (Y)
LIM_3: CON_ENCODER1.7, V1.6 (Y)
LIM_4: CON_ENCODER1.6, V1.10 (Y), V4.2 (B)
OPTO_1: OPTO-ACOPLADOR1.3, R8.1, TP5.TP, V1.1 (A)
OPTO_2: OPTO-ACOPLADOR1.4, R9.1, TP6.TP
OPTO_3: OPTO-ACOPLADOR1.5, R11.1, TP7.TP, V1.5 (A)
OPTO_4: OPTO-ACOPLADOR1.6, R10.1, TP8.TP, V1.11 (A)
OPTP_2: V1.3 (A)
PH_A: CON_ENCODER1.15; also elsewhere on the board
PH_B: CON_ENCODER1.12; also elsewhere on the board
SCL: CON_ENCODER1.8
SDA: CON_ENCODER1.5
SON_ON: CON_ENCODER1.3, V1.12 (Y)
VCC: C4.1, C5.1, CON_ENCODER1.2, OPTO-ACOPLADOR1.1, R8.2, R9.2, R10.2, R11.2, TP1.TP, V1.14 (+UB), V4.14 (+UB); also elsewhere on the board
VDD: CON_ENCODER1.13; also elsewhere on the board

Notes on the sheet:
Compuerta NAND
Compuerta NOT con Schmitt Trigger
Conector IDC - 16 pines
Salidas de sesores - optoacopladores
La salida de EMERGENCIA se activan con los opto-acopladores Lim_1 y Lim_4
La salida de ALARMA se activa con los optpacopladores Lim_2 y Lim_3

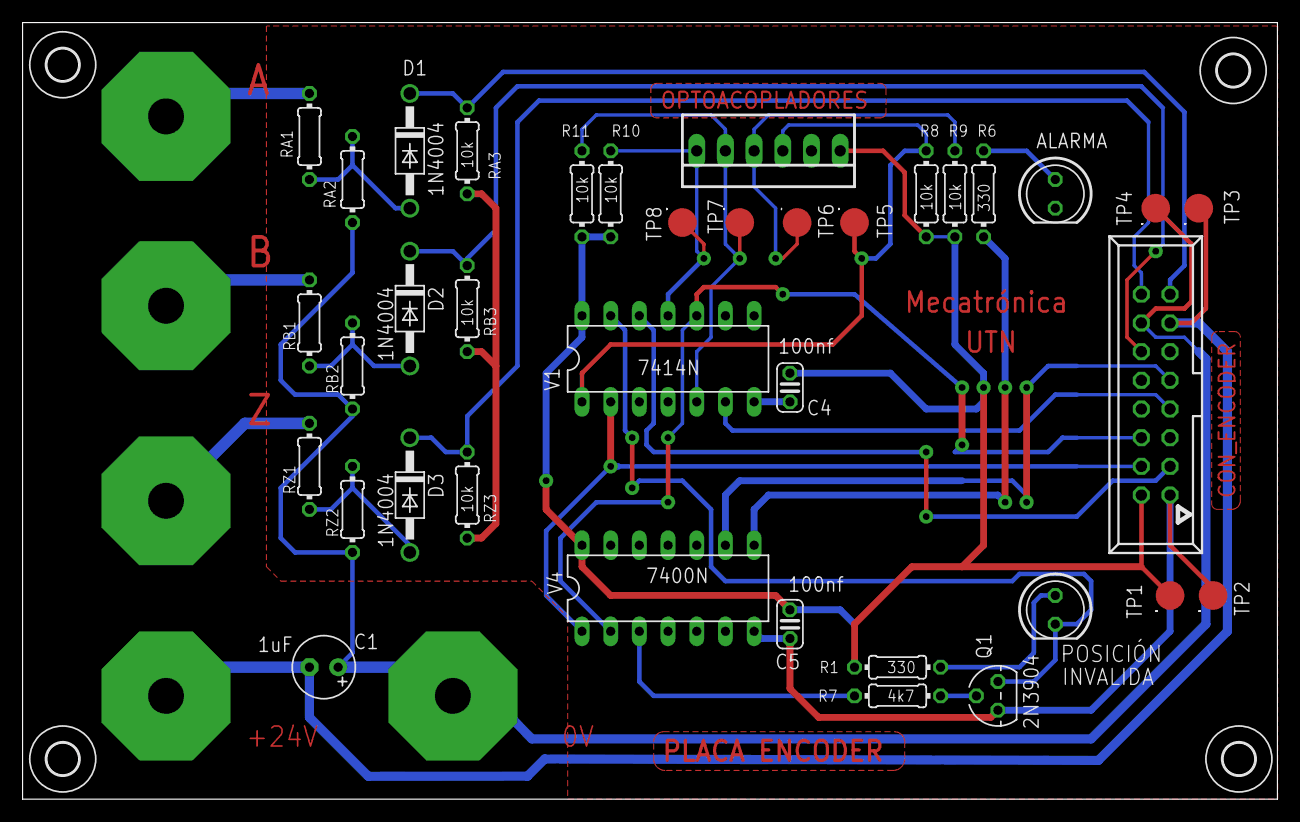
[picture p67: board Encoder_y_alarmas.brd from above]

Board: 2 copper layers, 111.1 x 68.8 mm, 46 parts (0 on the bottom side), 28 nets.

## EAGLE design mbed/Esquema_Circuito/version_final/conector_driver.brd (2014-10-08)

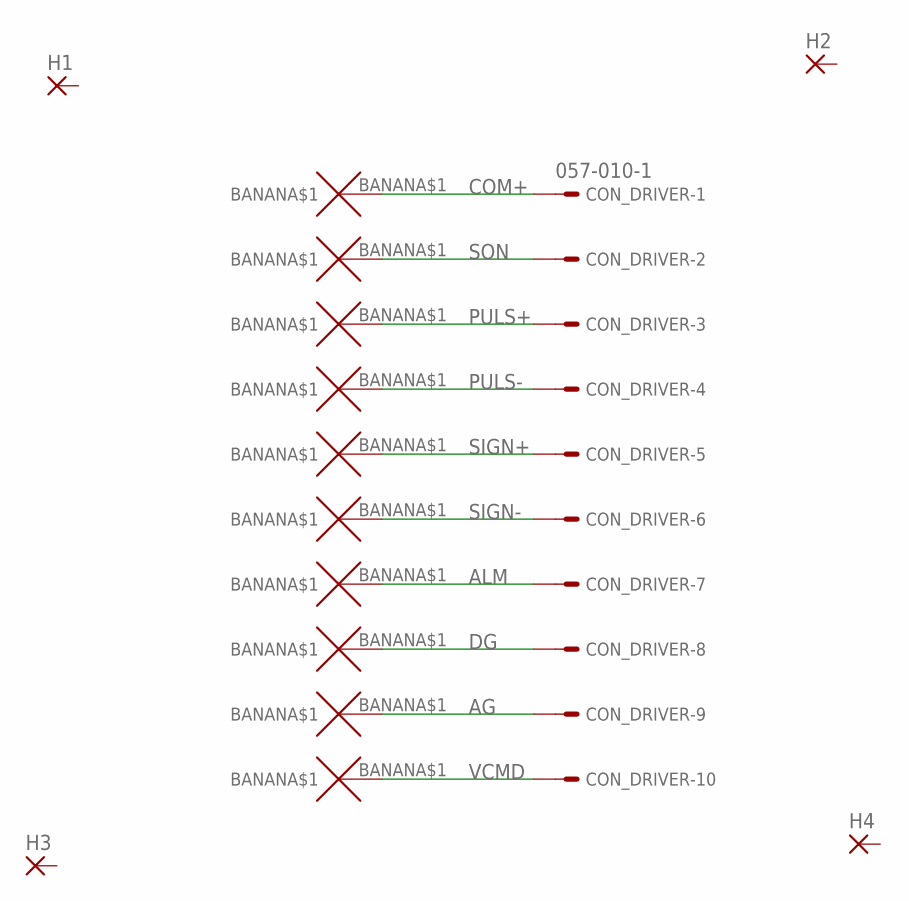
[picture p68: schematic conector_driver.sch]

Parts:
AG: BANANA
ALM: BANANA
COM+: BANANA
CON_DRIVER: 057-010-1
DG: BANANA
H1, H2, H3, H4: 3,81/1,4
PULS+: BANANA
PULS-: BANANA
SIGN+: BANANA
SIGN-: BANANA
SON: BANANA
VCMD: BANANA

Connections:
AG: AG.BANANA$1, CON_DRIVER.9
ALM: ALM.BANANA$1, CON_DRIVER.7
COM+: COM+.BANANA$1, CON_DRIVER.1
DG: CON_DRIVER.8, DG.BANANA$1
PULS+: CON_DRIVER.3, PULS+.BANANA$1
PULS-: CON_DRIVER.4, PULS-.BANANA$1
SIGN+: CON_DRIVER.5, SIGN+.BANANA$1
SIGN-: CON_DRIVER.6, SIGN-.BANANA$1
SON: CON_DRIVER.2, SON.BANANA$1
VCMD: CON_DRIVER.10, VCMD.BANANA$1

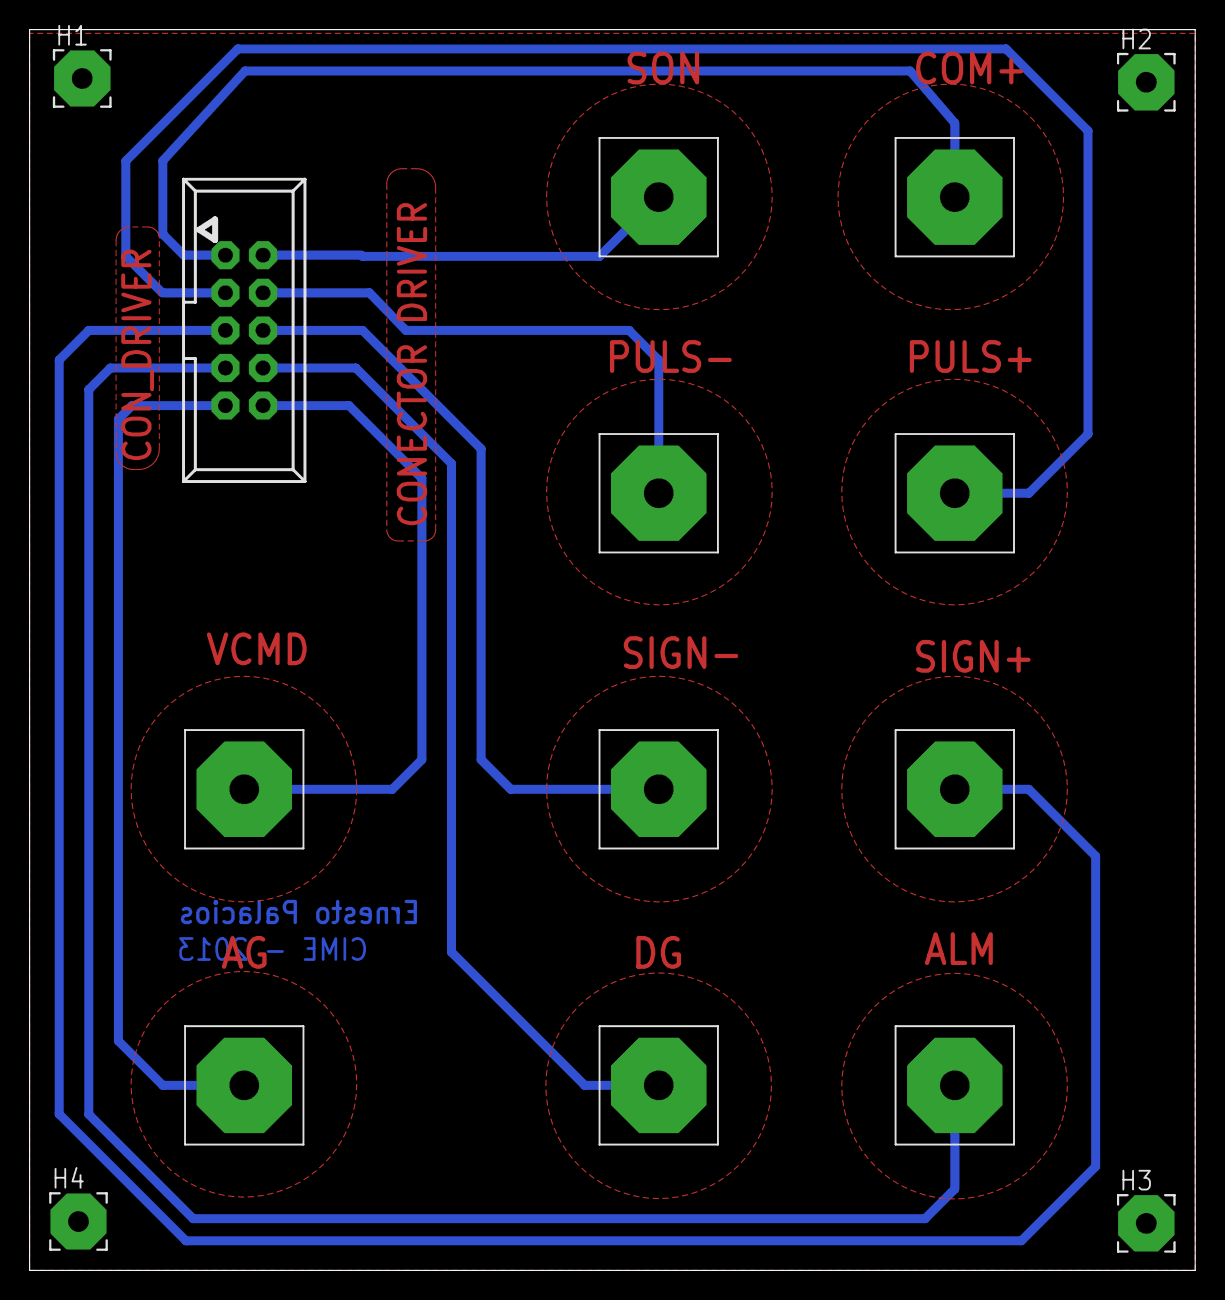
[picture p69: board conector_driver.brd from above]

Board: 2 copper layers, 78.7 x 83.8 mm, 15 parts (0 on the bottom side), 10 nets.

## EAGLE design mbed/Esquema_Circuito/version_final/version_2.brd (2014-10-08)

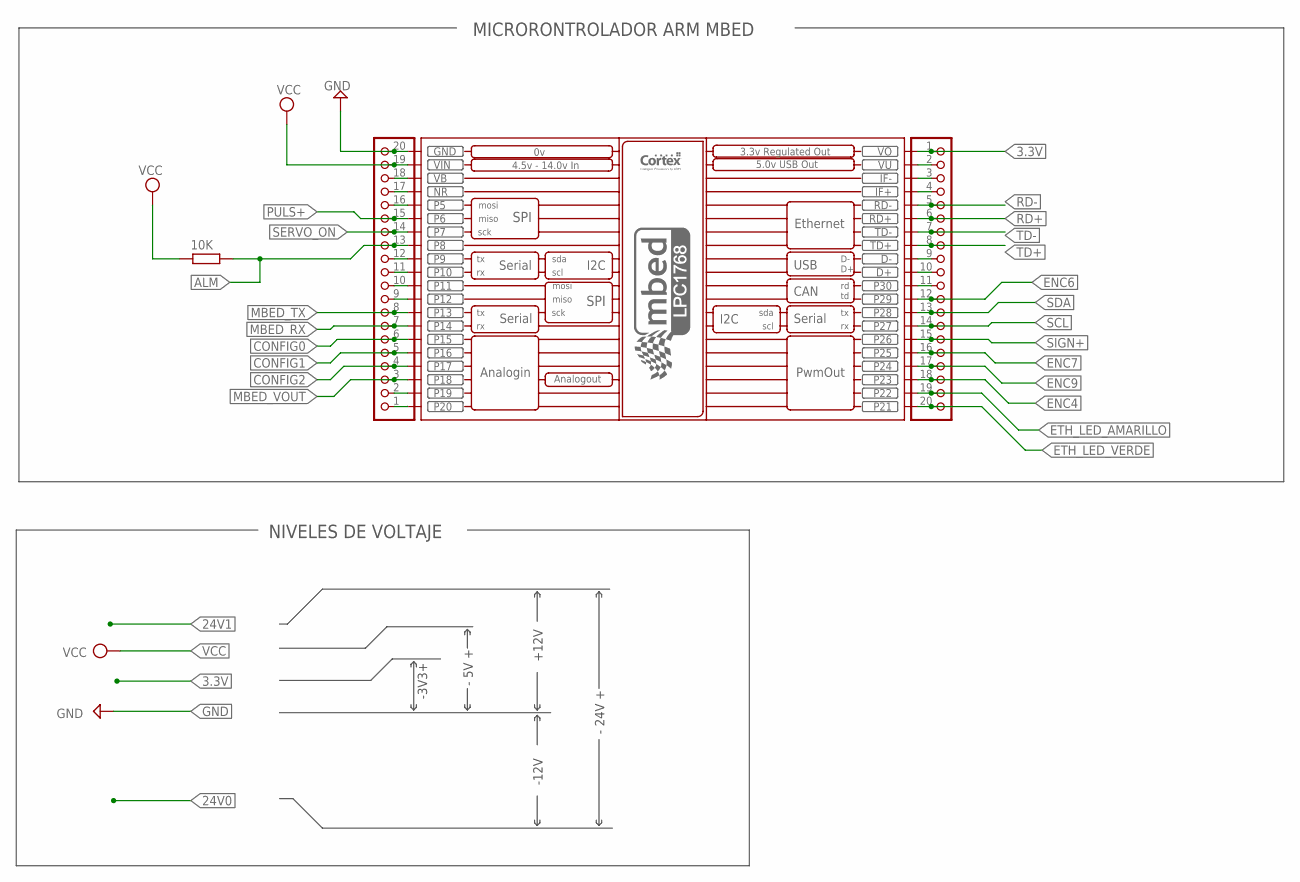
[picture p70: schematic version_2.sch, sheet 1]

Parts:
JP_LEFT: PINHD-1X20; 1X20
JP_RIGHT: PINHD-1X20; 1X20
KIT1: MBED_NXP_LPC1768; MBED-KIT
R16_ALM: 10K; 0207/12

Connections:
3.3V: JP_RIGHT.1, KIT1.VOUT (VO); also elsewhere on the board
ALM: JP_LEFT.13, KIT1.P$8 (P8), R16_ALM.1; also elsewhere on the board
CONFIG0: JP_LEFT.6, KIT1.P$15 (P15); also elsewhere on the board
CONFIG1: JP_LEFT.5, KIT1.P$16 (P16); also elsewhere on the board
CONFIG2: JP_LEFT.4, KIT1.P$17 (P17); also elsewhere on the board
ENC4: JP_RIGHT.18, KIT1.P$23 (P23); also elsewhere on the board
ENC6: JP_RIGHT.12, KIT1.P$29 (P29); also elsewhere on the board
ENC7: JP_RIGHT.16, KIT1.P$25 (P25); also elsewhere on the board
ENC9: JP_RIGHT.17, KIT1.P$24 (P24); also elsewhere on the board
ETH_LED_AMARILLO: JP_RIGHT.19, KIT1.P$22 (P22); also elsewhere on the board
ETH_LED_VERDE: JP_RIGHT.20, KIT1.P$21 (P21); also elsewhere on the board
GND: JP_LEFT.20, KIT1.GND; also elsewhere on the board
MBED_RX: JP_LEFT.7, KIT1.P$14 (P14); also elsewhere on the board
MBED_TX: JP_LEFT.8, KIT1.P$13 (P13); also elsewhere on the board
MBED_VOUT: JP_LEFT.3, KIT1.P$18 (P18); also elsewhere on the board
unnamed: JP_LEFT.12, KIT1.P$9 (P9)
unnamed: JP_RIGHT.2, KIT1.VU
unnamed: JP_LEFT.11, KIT1.P$10 (P10)
unnamed: JP_RIGHT.3, KIT1.IF-
unnamed: JP_RIGHT.4, KIT1.IF+
unnamed: JP_RIGHT.11, KIT1.P$30 (P30)
unnamed: JP_RIGHT.9, KIT1.D-
unnamed: JP_RIGHT.10, KIT1.D+
unnamed: JP_LEFT.18, KIT1.VB
unnamed: JP_LEFT.17, KIT1.NR
unnamed: JP_LEFT.16, KIT1.P$5 (P5)
unnamed: JP_LEFT.10, KIT1.P$11 (P11)
unnamed: JP_LEFT.9, KIT1.P$12 (P12)
unnamed: JP_LEFT.2, KIT1.P$19 (P19)
unnamed: JP_LEFT.1, KIT1.P$20 (P20)
PULS+: JP_LEFT.15, KIT1.P$6 (P6); also elsewhere on the board
RD+: JP_RIGHT.6, KIT1.RD+; also elsewhere on the board
RD-: JP_RIGHT.5, KIT1.RD-; also elsewhere on the board
SCL: JP_RIGHT.14, KIT1.P$27 (P27); also elsewhere on the board
SDA: JP_RIGHT.13, KIT1.P$28 (P28); also elsewhere on the board
SERVO_ON: JP_LEFT.14, KIT1.P$7 (P7); also elsewhere on the board
SIGN+: JP_RIGHT.15, KIT1.P$26 (P26); also elsewhere on the board
TD+: JP_RIGHT.8, KIT1.TD+; also elsewhere on the board
TD-: JP_RIGHT.7, KIT1.TD-; also elsewhere on the board
VCC: JP_LEFT.19, KIT1.VIN, R16_ALM.2; also elsewhere on the board

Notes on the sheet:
- 24V +
- 5V +
-3V3+
+12V
-12V
NIVELES DE VOLTAJE
MICRORONTROLADOR ARM MBED

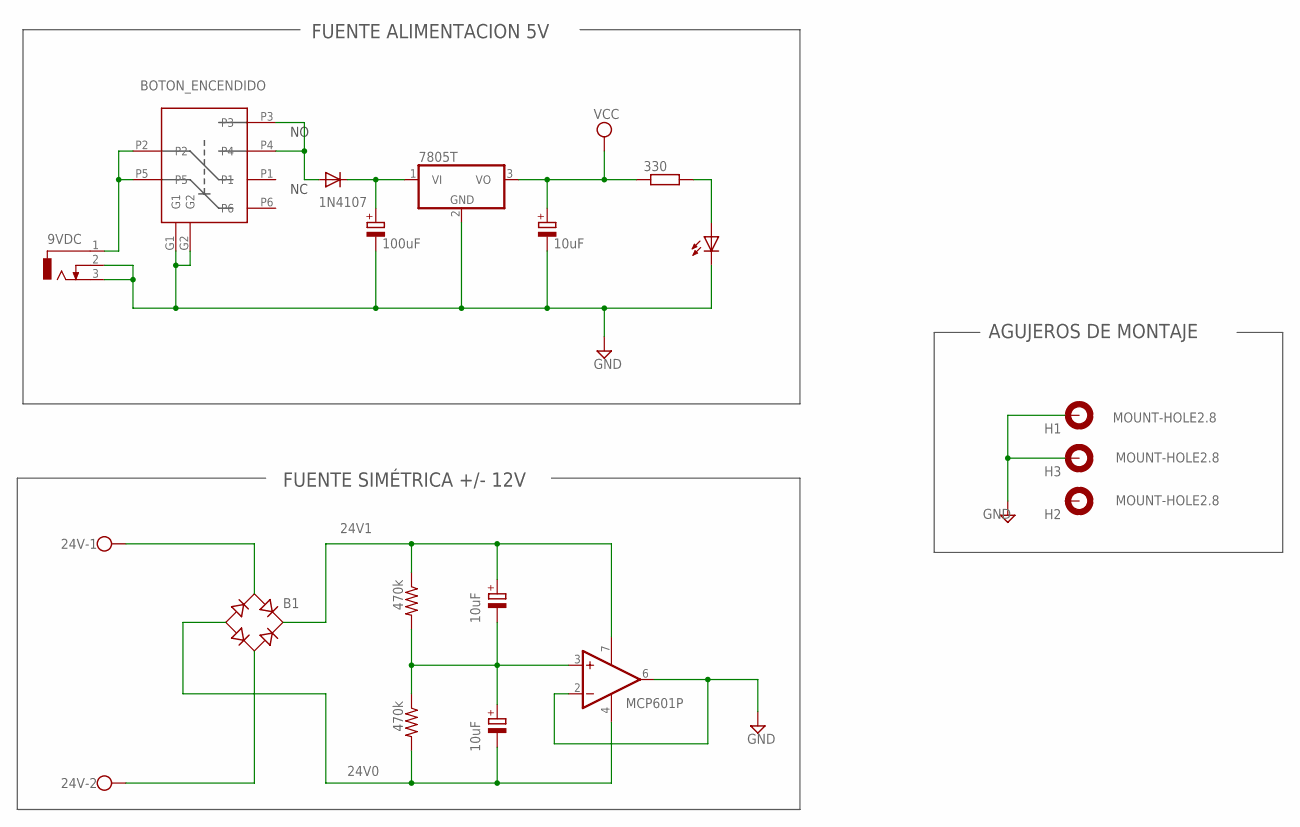
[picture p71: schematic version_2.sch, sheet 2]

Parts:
9VDC: DCJ0303
24V: W237-02P; W237-132
B1: RB1A
C1_9V: 100uF; TT5D7
C1_+24, C2_0V, C2_9V: 10uF; TT5D7
D1_INPUT: 1N4107; DO35-10
H1, H2, H3: MOUNT-HOLE2.8; 3,3-PAD
IC2: 7805T; TO220H
IC3: MCP601P; DIL08
ON/OFF: BOTON_ENCENDIDO; BOTON_ENCNEDIDO
POWER: LED3MM
PWR_LED_R: 330; 0204/7
R1_DIV, R2_DIV: 470k; 0207/10

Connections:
24V0: B1.-, C2_0V.-, IC3.4 (V-), R2_DIV.2; also elsewhere on the board
24V1: B1.+, C1_+24.+, IC3.7 (V+), R1_DIV.1; also elsewhere on the board
GND: 9VDC.2, 9VDC.3, C1_9V.-, C2_9V.-, H1.B3,3, H3.B3,3, IC2.2 (GND), IC3.2 (-IN), IC3.6 (OUT), ON/OFF.G1, ON/OFF.G2, POWER.K (C); also elsewhere on the board
unnamed: 24V.1, B1.AC1
unnamed: 24V.2, B1.AC2
unnamed: C1_+24.-, C2_0V.+, IC3.3 (+IN), R1_DIV.2, R2_DIV.1
unnamed: D1_INPUT.A, ON/OFF.P3, ON/OFF.P4
unnamed: 9VDC.1, ON/OFF.P2, ON/OFF.P5
unnamed: C1_9V.+, D1_INPUT.C, IC2.1 (VI)
unnamed: POWER.A, PWR_LED_R.2
VCC: C2_9V.+, IC2.3 (VO), PWR_LED_R.1; also elsewhere on the board

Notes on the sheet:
FUENTE ALIMENTACION 5V
FUENTE SIMÉTRICA +/- 12V
AGUJEROS DE MONTAJE

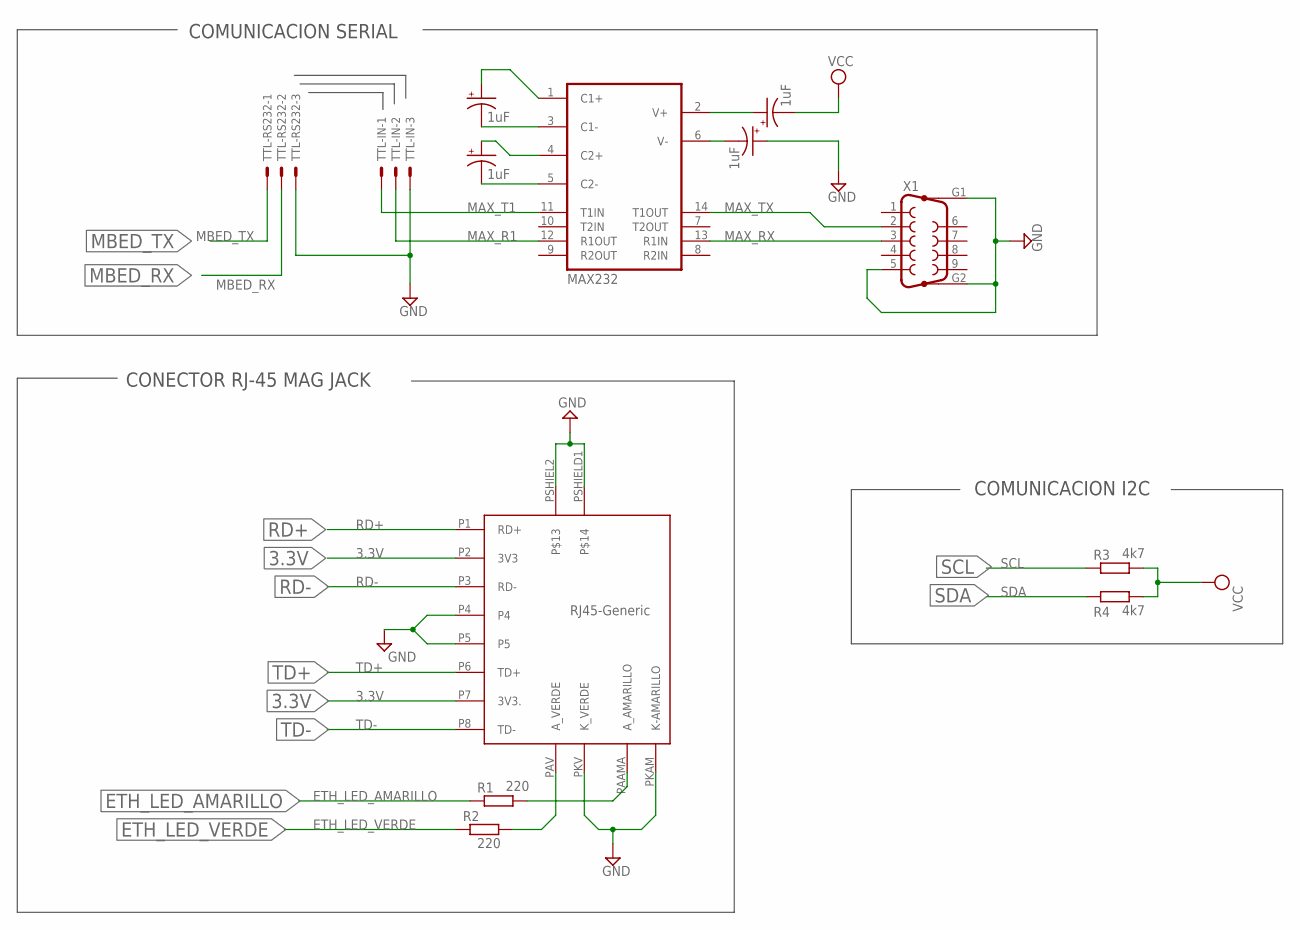
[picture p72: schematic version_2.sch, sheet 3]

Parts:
C1_MAX, C2_MAX, C3_MAX, C4_MAX: 1uF; E2,5-6E
IC1: MAX232; DIL16
R1, R2: 220; 0207/15
R3, R4: 4k7; 0204/7
TTL-IN: 22-23-2031
TTL-RS232: 22-23-2031
U$1: RJ-45-GENERIC; RJ45-GENERIC
X1: F09HP

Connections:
3.3V: U$1.P2 (3V3), U$1.P7 (3V3.); also elsewhere on the board
ETH_LED_AMARILLO: R1.1; also elsewhere on the board
ETH_LED_VERDE: R2.1; also elsewhere on the board
GND: C3_MAX.+, IC1.15 (GND), TTL-IN.3, TTL-RS232.3, U$1.P4, U$1.P5, U$1.PKAM (K-AMARILLO), U$1.PKV (K_VERDE), U$1.PSHIEL2, U$1.PSHIELD1, X1.5, X1.G1, X1.G2; also elsewhere on the board
MAX_R1: IC1.12 (R1OUT), TTL-IN.2
MAX_RX: IC1.13 (R1IN), X1.3; also elsewhere on the board
MAX_T1: IC1.11 (T1IN), TTL-IN.1
MAX_TX: IC1.14 (T1OUT), X1.2; also elsewhere on the board
MBED_RX: TTL-RS232.2; also elsewhere on the board
MBED_TX: TTL-RS232.1; also elsewhere on the board
unnamed: C1_MAX.+, IC1.1 (C1+)
unnamed: C1_MAX.-, IC1.3 (C1-)
unnamed: C2_MAX.-, IC1.5 (C2-)
unnamed: C2_MAX.+, IC1.4 (C2+)
unnamed: C4_MAX.+, IC1.2 (V+)
unnamed: C3_MAX.-, IC1.6 (V-)
unnamed: R1.2, U$1.PAAMA (A_AMARILLO)
unnamed: R2.2, U$1.PAV (A_VERDE)
RD+: U$1.P1 (RD+); also elsewhere on the board
RD-: U$1.P3 (RD-); also elsewhere on the board
SCL: R3.1; also elsewhere on the board
SDA: R4.1; also elsewhere on the board
TD+: U$1.P6 (TD+); also elsewhere on the board
TD-: U$1.P8 (TD-); also elsewhere on the board
VCC: C4_MAX.-, IC1.16 (VCC), R3.2, R4.2; also elsewhere on the board

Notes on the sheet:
CONECTOR RJ-45 MAG JACK
COMUNICACION SERIAL
COMUNICACION I2C

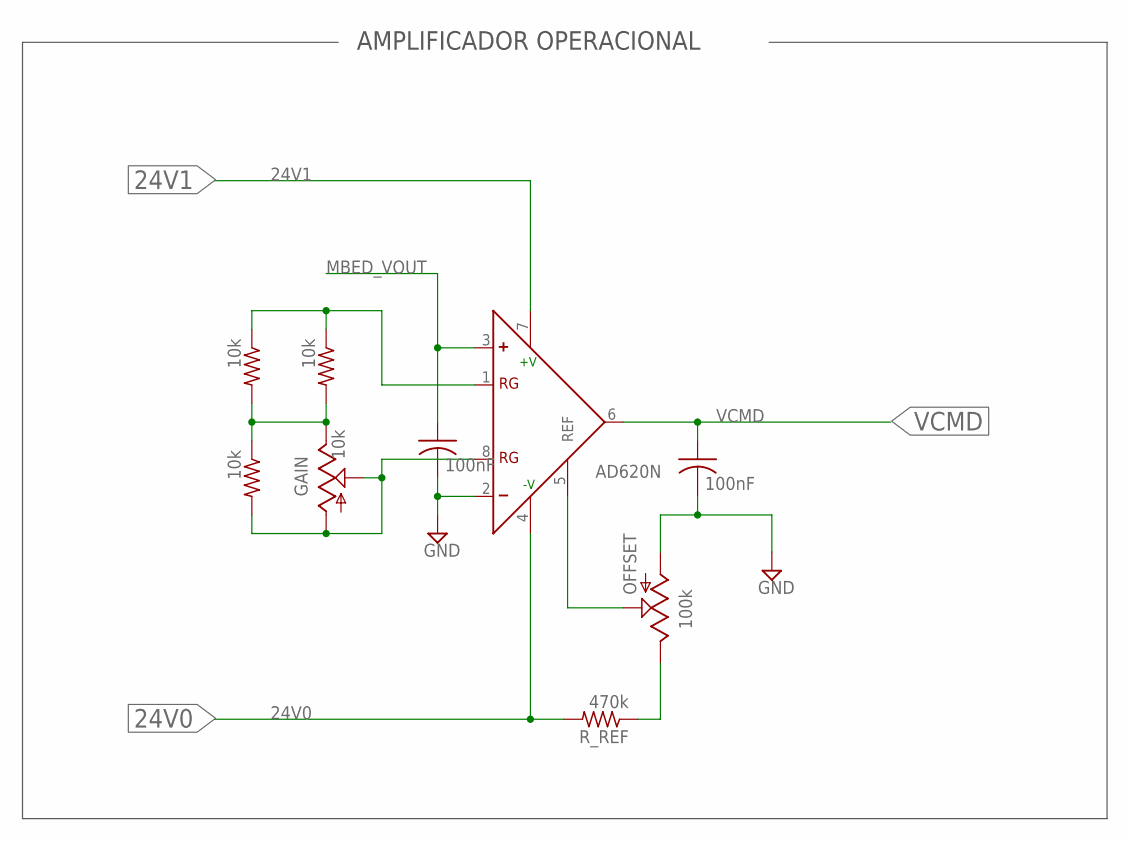
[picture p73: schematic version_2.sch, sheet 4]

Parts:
C3_AOUT, C5_AOUT: 100nF; C025-024X044
GAIN: 10k; RJ9W
IC4: AD620N; DIL08
OFFSET: 100k; RJ9W
R1_G, R2_G, R3_G: 10k; 0204/7
R_REF: 470k; 0204/7

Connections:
24V0: IC4.4 (-V), R_REF.2; also elsewhere on the board
24V1: IC4.7 (+V); also elsewhere on the board
GND: C3_AOUT.2, C5_AOUT.2, IC4.2 (-), OFFSET.A; also elsewhere on the board
MBED_VOUT: C5_AOUT.1, IC4.3 (+); also elsewhere on the board
unnamed: OFFSET.E, R_REF.1
unnamed: IC4.1 (RG), R1_G.1, R3_G.1
unnamed: GAIN.E, R1_G.2, R2_G.1, R3_G.2
unnamed: GAIN.A, GAIN.S, IC4.8 (RG), R2_G.2
unnamed: IC4.5 (REF), OFFSET.S
VCMD: C3_AOUT.1, IC4.6 (OUT); also elsewhere on the board

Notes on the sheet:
AMPLIFICADOR OPERACIONAL

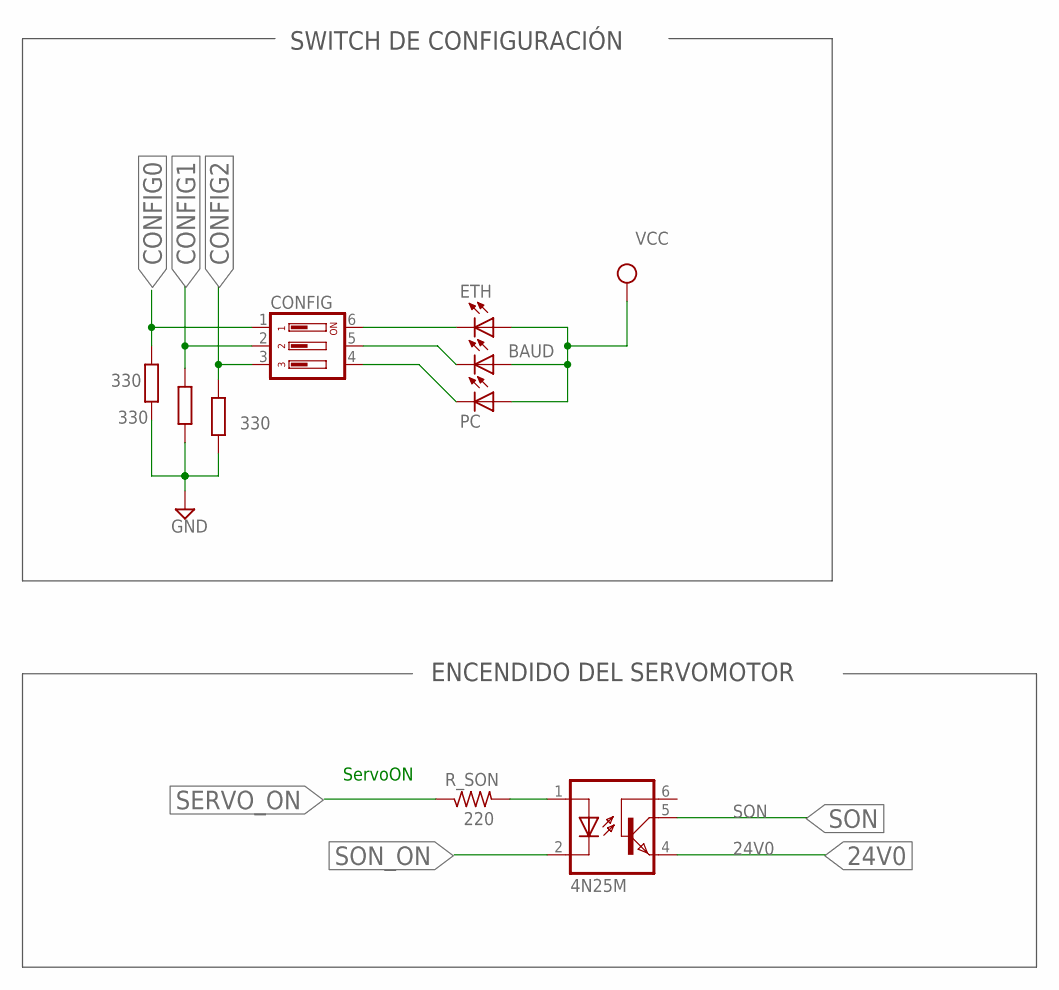
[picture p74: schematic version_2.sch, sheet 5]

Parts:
BAUD: LED3MM
CONFIG: DIP03YL
ETH: LED3MM
OK1: 4N25M; DIL06
PC: LED3MM
R13, R14, R15: 330; 0204/7
R_SON: 220; 0207/7

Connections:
24V0: OK1.4 (EMI); also elsewhere on the board
CONFIG0: CONFIG.1, R15.2; also elsewhere on the board
CONFIG1: CONFIG.2, R14.2; also elsewhere on the board
CONFIG2: CONFIG.3, R13.2; also elsewhere on the board
GND: R13.1, R14.1, R15.1; also elsewhere on the board
unnamed: OK1.1 (A), R_SON.2
unnamed: CONFIG.6, ETH.K (C)
unnamed: BAUD.K (C), CONFIG.5
unnamed: CONFIG.4, PC.K (C)
SERVO_ON: R_SON.1; also elsewhere on the board
SON: OK1.5 (COL); also elsewhere on the board
SON_ON: OK1.2 (C); also elsewhere on the board
VCC: BAUD.A, ETH.A, PC.A; also elsewhere on the board

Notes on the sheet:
ServoON
SWITCH DE CONFIGURACIÓN
ENCENDIDO DEL SERVOMOTOR

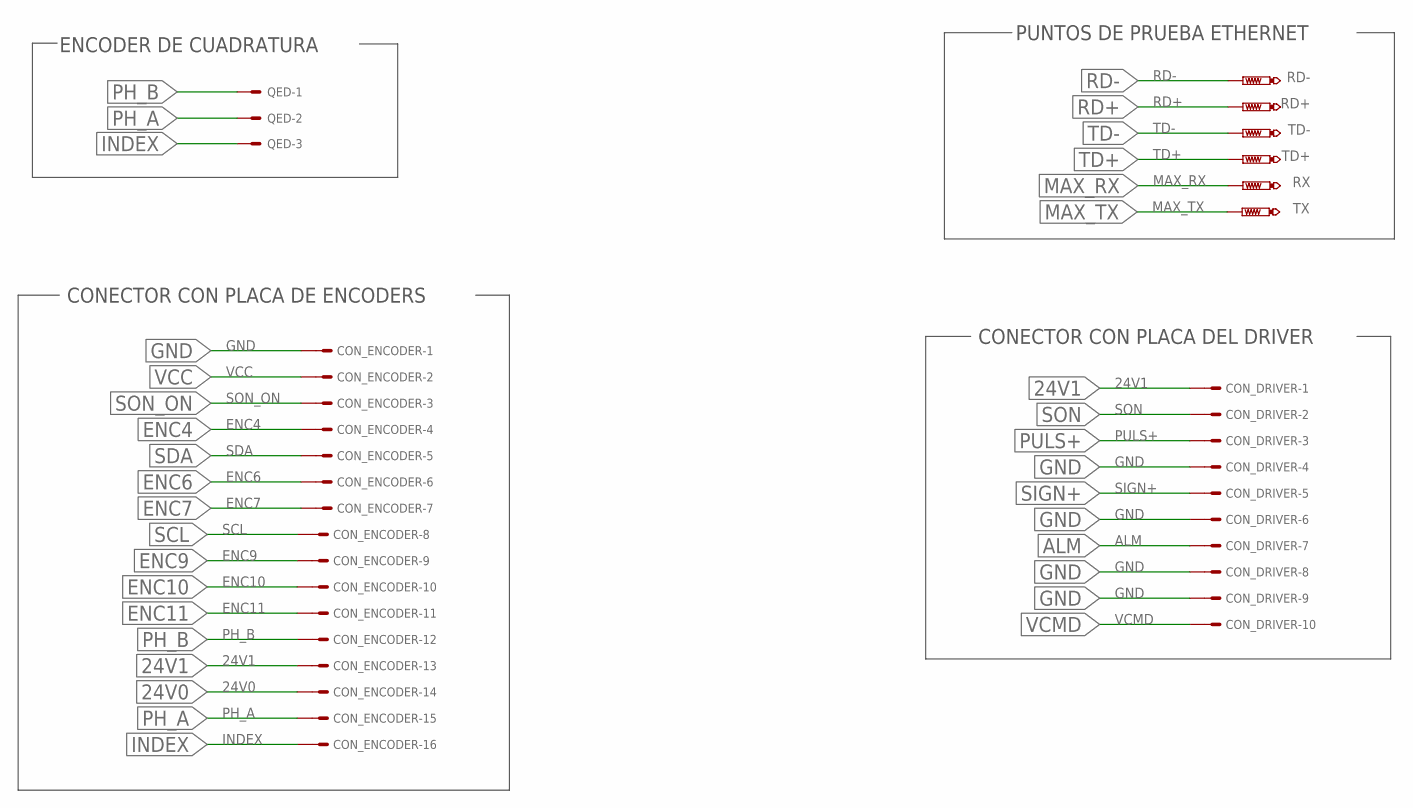
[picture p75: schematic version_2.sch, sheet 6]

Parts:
CON_DRIVER: 057-010-1
CON_ENCODER: 057-016-1
QED: 22-23-2031
RD+: PTR1PAD1-13Y; P1-13Y
RD-: PTR1PAD1-13Y; P1-13Y
RX: PTR1PAD1-13Y; P1-13Y
TD+: PTR1PAD1-13Y; P1-13Y
TD-: PTR1PAD1-13Y; P1-13Y
TX: PTR1PAD1-13Y; P1-13Y

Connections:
24V0: CON_ENCODER.14; also elsewhere on the board
24V1: CON_DRIVER.1, CON_ENCODER.13; also elsewhere on the board
ALM: CON_DRIVER.7; also elsewhere on the board
ENC4: CON_ENCODER.4; also elsewhere on the board
ENC6: CON_ENCODER.6; also elsewhere on the board
ENC7: CON_ENCODER.7; also elsewhere on the board
ENC9: CON_ENCODER.9; also elsewhere on the board
ENC10: CON_ENCODER.10
ENC11: CON_ENCODER.11
GND: CON_DRIVER.4, CON_DRIVER.6, CON_DRIVER.8, CON_DRIVER.9, CON_ENCODER.1; also elsewhere on the board
INDEX: CON_ENCODER.16, QED.3
MAX_RX: RX.TP; also elsewhere on the board
MAX_TX: TX.TP; also elsewhere on the board
PH_A: CON_ENCODER.15, QED.2
PH_B: CON_ENCODER.12, QED.1
PULS+: CON_DRIVER.3; also elsewhere on the board
RD+: RD+.TP; also elsewhere on the board
RD-: RD-.TP; also elsewhere on the board
SCL: CON_ENCODER.8; also elsewhere on the board
SDA: CON_ENCODER.5; also elsewhere on the board
SIGN+: CON_DRIVER.5; also elsewhere on the board
SON: CON_DRIVER.2; also elsewhere on the board
SON_ON: CON_ENCODER.3; also elsewhere on the board
TD+: TD+.TP; also elsewhere on the board
TD-: TD-.TP; also elsewhere on the board
VCC: CON_ENCODER.2; also elsewhere on the board
VCMD: CON_DRIVER.10; also elsewhere on the board

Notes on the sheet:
ENCODER DE CUADRATURA
PUNTOS DE PRUEBA ETHERNET
CONECTOR CON PLACA DE ENCODERS
CONECTOR CON PLACA DEL DRIVER

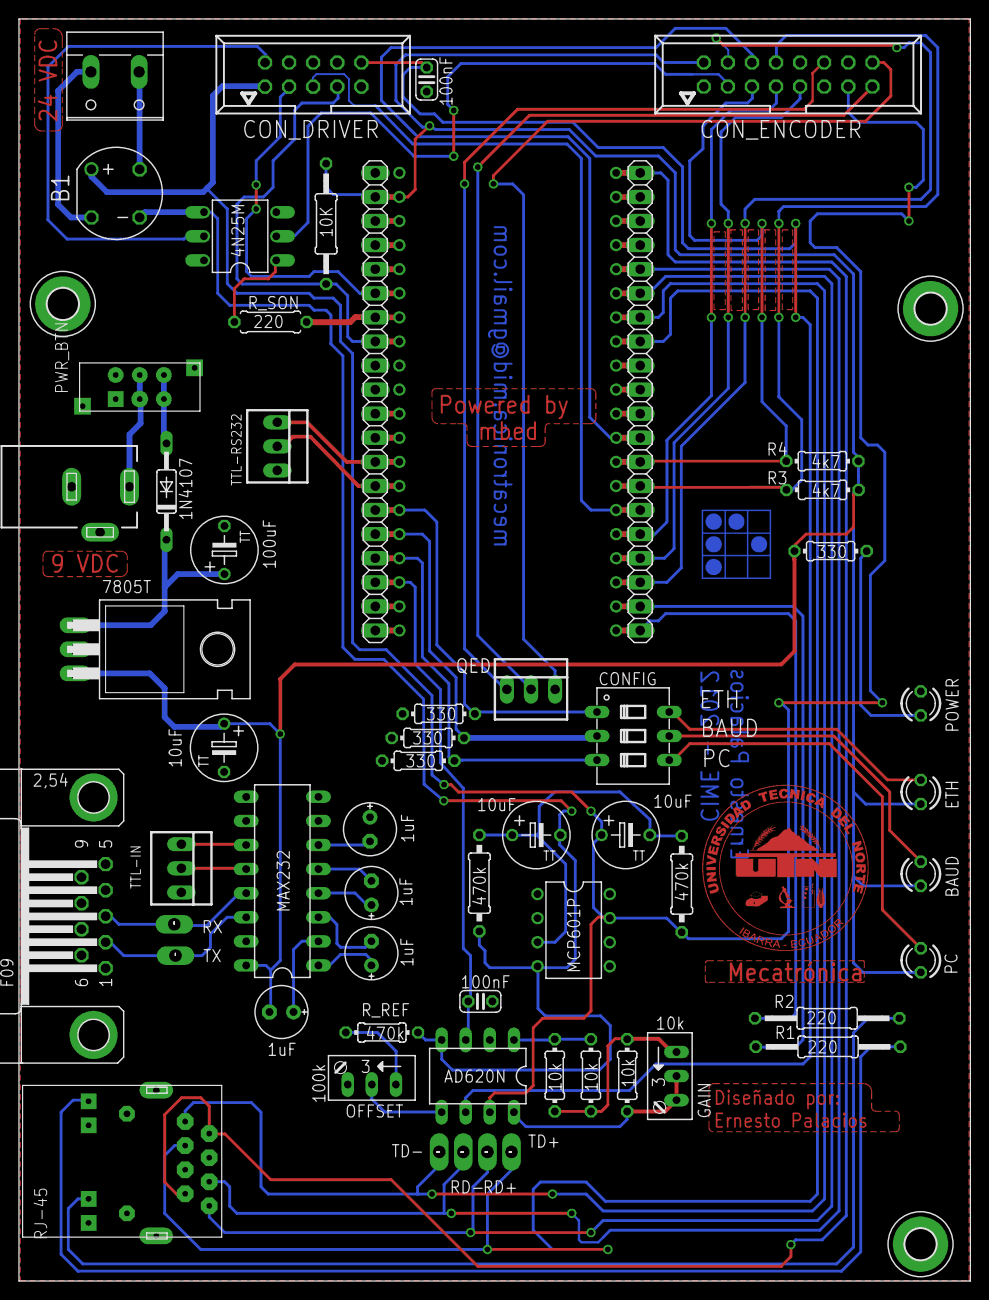
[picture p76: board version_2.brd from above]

Board: 2 copper layers, 100.3 x 133.1 mm, 62 parts (0 on the bottom side), 76 nets.

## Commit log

2014-10-08 Añadidos archivos base
    [ATtiny_Decoder.DSN, Acople nuez.SLDPRT, Deslizador Base.SLDPRT, ENC_CON.brd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]
2014-11-22 Se separo el archivo TrabajodeGrado en varios archivos y un PDF
    [ATtiny_Decoder.DSN, ENC_CON.brd, ENC_CON.sch, LoveJoy.SLDPRT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]
2014-11-23 Añadido archivo de tesis y removido .ini
2015-01-25 Update README.md
    Enlace al manual de ayuda
